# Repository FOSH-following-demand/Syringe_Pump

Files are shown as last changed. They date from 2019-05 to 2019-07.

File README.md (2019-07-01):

# Syringe Pump
<p align="center">
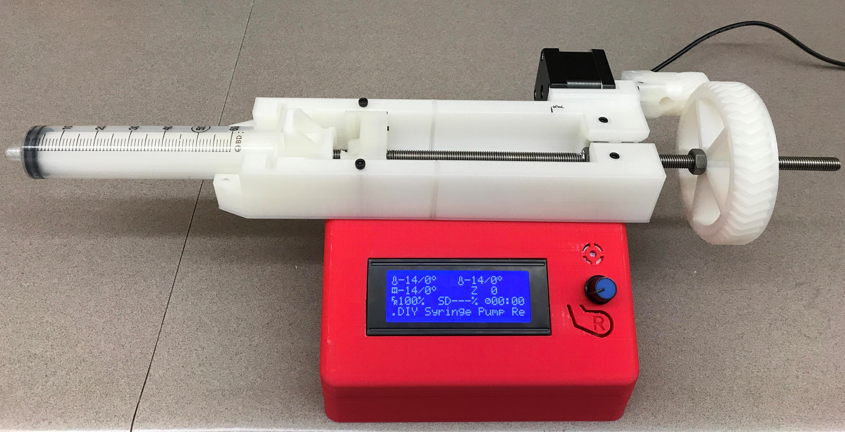
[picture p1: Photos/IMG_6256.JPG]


We are a team of 4 people from Utah, USA. We creating a open source DIY syringe pump from commonly available and 3D printed parts that allows for high accuracy and repeatability. We also want to make this project as simple as possible so that no specialized skills are required.

The syringe pump that will be built will then be able to be integrated with almost any commonly available desktop 3D printer to create a [bioprinter](https://github.com/FOSH-following-demand/Bioprinter).

We would like to give credit to Kira Puscha, Thomas J.Hinton, and Adam W.Feinberg at Carnegie for their work on the [Large volume syringe pump extruder for desktop 3D printers](https://www.sciencedirect.com/science/article/pii/S2468067217300822#!) that served for the basis and inspiration for this project

If you have any questions or get involved, get in contact with us via email at drewcliffporter@gmail.com

## Getting Started

Follow these links to learn about this project, and to get started building your own syringe pump!
- [Large Volume Syringe Pump Extruder](https://www.sciencedirect.com/science/article/pii/S2468067217300822#!)
- [Parts to purchase](Bill_of_Materials)
- [Parts to 3D print](3D_Printed_Parts.csv)
- [Assembly](Assembly_Instructions.md)
- [Troubleshooting](Troubleshooting.md)
- [Firmware](Firmware)
- [Calibration](Calibration.md)
- [Using your new pump](Getting_Started.md)
## Progress

Week 1:
- Identified parts to order
- Learned how to use Github (to an extent)
-

Week 2:
- Got parts in
- Started assembly of syringe pump
-

Week 3:
- Finished assembly of syringe pump
- Started Programing
- Began troubleshooting

Week 4:
- Continued programming
- began working on the bioprinter
- Printed Control Box

Week 5:
- Calibration
- Integration into the bioprinter
- Code Tweaks

Week 6:
- Started Bioprinting
- Failed at bioprinting
- Almost finished the GitHub repository

Week 7:
- Got some advice from Advanced BioMatrix
- Ordered a different gelatin
- Researched different "bioinks"
- Tried to print with different materials (agarose, calcium phosphate, frosting), but none worked

Week 8:
-
-
-

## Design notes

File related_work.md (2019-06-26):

# Related projects

Use this file to store updated information on projects similar to yours. You will start it on week 1 and probably keep updating it as you find more similar projects.

Make sure each reference meets the minimum requirements (url, active/non active, notes on how it's useful for you), and feel free to add other useful fields.

Look below for a template. For a markdown cheatsheet, check [this repo](https://github.com/adam-p/markdown-here/wiki/Markdown-Cheatsheet#tables).

| Project name  | URL           | Active/Not active | Notes - relevance |
| ------------- | ------------- | ----------------- | -------------- |
| Large volume syringe pump extruder for desktop 3D printers | https://www.sciencedirect.com/science/article/pii/S2468067217300822#! | Active | Favorite method so far, accurate dispensing of the liquid, requires less hardware to be purchased, only one size of syringe, retraction enabled, Doesn't work separate from a 3D printer |
| Open-Source Syringe Pump Library | https://www.academia.edu/8369549/Open-Source_Syringe_Pump_Library | Not Active | Can be used for any size syringe |
| Open-source syringe pump | https://www.appropedia.org/Open-source_syringe_pump | Active | Using similar method as we plan to use, however we believe ours will have a greater accuracy at small volumes, must have a computer to control, cannot be controlled with a Windows computer |

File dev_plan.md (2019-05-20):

# Development plan

Use this file to store your plan for the program. What are you going to do, in which order?

| Week        | Activities           | Who           |
| ----------- | -------------------- | ------------- |
| 1           | Create GitHub repo, familiarize with GitHub, first call with mentor, identify similar projects, identify parts to order  |Drew, All|
| 2           | Order parts, second call, more research into similar projects | Drew, All |
| 3           | Start Assembly, Start coding, Start designing/printing, third call | Drew, AJ, All |
| 4           | Finish assembly and code, start testing and calibration, fourth call | All |
| 5           | Finish testing and calibration, make any necessary changes, fifth call | All |
| 6           | Troubleshoot bioprints and create documentation for good bioprints, sixth call | Drew |
| 7           | Make sure the repository is accurate and informative, seventh call | All |
| 8           | Buffer week                     |               |

# Syringe Pump plan

We plan on using easy to use, off the shelf components, 3D printed parts, and easily accessible code to develop the pump. We want to create the pump in such a way that minimal skills will be required for the assembly and use. Therefore things such as soldering should be avoided. To avoid soldering we will be using an Arduino Mega board that has stepper motor drivers built in. We also want the unit to be self contained and not require the input from a computer to control the dispensing of the liquid.

 We also plan on using open sourced firmware that is originally for 3D printers for the syringe pump. That makes it so that we don't have to reinvent the wheel, and up to five syringe pumps can be controlled from a single control board. This also allows for upgrades to the pump if the user desires, such as endstops and thermal regulation. The use of 3D printer firmware allows for the user to create a program in the easy to learn language of G-Code that could complete a series of tasks, without the user having to interact with the pump controls.

 In harmony with the second part of our project, a 3D printed housing will be produced to house all of the electronics.

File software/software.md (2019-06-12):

The software for this pump is based on the open source firmware for 3D printers. The firmware we used is called Marlin, and can be found here http://marlinfw.org/. We used version 1.1 in this build, and made modifications to allow the firmware to best serve its purpose in this syringe pump.

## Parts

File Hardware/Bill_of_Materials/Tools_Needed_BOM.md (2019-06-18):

# Necessary

- M3 allen wrench
- M8 allen Wrench
- Drill
- 7/64th drill bit
- needle nose or slipjoint pliers

# Optional

- Tweezers

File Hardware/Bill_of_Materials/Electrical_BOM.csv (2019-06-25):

Item | Quantity | Cost | Source
MKS-Base v1.6 | 1 | 34.99 | https://www.amazon.com/BIQU-MKS-Base-Plate-Controller-Printer/dp/B076S2SDQ9
Smart Display | 1 | 10.99 | https://www.amazon.com/BIQU-Display-Controller-2004LCD-Adapter/dp/B01FLU9X5Q
NEMA 17 Stepper Motor | 1 | 9.99 | https://www.amazon.com/UsongShine-Nema17-Stepper-17HS4401S-Printer/dp/B0787BQ4WH?s=gateway
Power Supply 12V 5A | 1 | 7.95 | https://www.ebay.com/itm/AC100-240V-To-DC-12V-1-2-3-5-6-8A-US-Power-Supply-Adapter-Transformer-LED-Strip/202127822979
TOTAL |  | 63.92
Note: A smaller Arduino such as the Arduino Uno could be used instead of the MKS-Base.
But if this approach is used separate stepper motor drivers must be purchased
and the code provided here might not work. The price ends up being comparable
in the end for both methods.

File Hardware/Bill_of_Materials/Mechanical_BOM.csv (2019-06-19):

Item | Quantity | Cost | Source
Double Shielded Ball Bearings | 2 | 5.98 | https://www.amazon.com/Onwon-Pieces-Skateboard-Bearings-Miniature/dp/B07LCJ9VM6?s=gateway
M8 2.4 mm Steel Hex Nuts | 4 | 4.84 | https://www.mcmaster.com/90592a022
M8 Brass Hex Nuts | 2 | 0.55 | https://www.fastenal.com/products/details/MN2580000BR0000
M8 1.25 by 300mm Threaded Rod Stainless Steel | 1 | 7.78 | https://www.mcmaster.com/90024a229
M3 10 mm Socket Head Screws (Hex Bolts) | 10 | 7.36 | https://www.mcmaster.com/91290a115
M3 16 mm Socket Head Screws (i.e. Hex Bolts) | 4 | 8.87 | https://www.mcmaster.com/91290a120
M3 8 mm Socket Head Screws (i.e. Hex Bolts) | 6 | 7.12 | https://www.mcmaster.com/91290a113
M3 45 mm Partially-Threaded Socket Head Screws (i.e. Hex Bolts) | 4 | 3.65 | https://www.mcmaster.com/91290a079
M3 Hex Nuts | 16 | 0.88 | https://www.mcmaster.com/90592a085
M3 x 8mm OD washers | 4 | 0.98 | https://www.mcmaster.com/93849a101
60 mL Luer-Lock BD Syringe | 1 | 33.31 | https://www.amazon.com/BD-60ml-CC-SYRINGE-ONLY/dp/B01EGL2WNG?s=industrial
PLA 1.75mm | 1 | 15-30
TOTAL |  | ~100
NOTE: |  |  | All the prices are for the minimum order requirement. Therefore the overall cost for one syringe pump is less than reported here. The parts also do not have to be bought from the sources listed here and could be found from a cheaper source.

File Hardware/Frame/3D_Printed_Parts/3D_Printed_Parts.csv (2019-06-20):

Name | Notes | Source
MKS Base 1.5 based desktop controller cabinet | Print with more than 3 walls and top/bottom layers. Supports are needed for the top | https://www.thingiverse.com/thing:3156697
Large Volume Syringe Pump Extruder (LVE) | Follow directions found here https://www.sciencedirect.com/science/article/pii/S2468067217300822#! | https://3dprint.nih.gov/discover/3DPX-008366

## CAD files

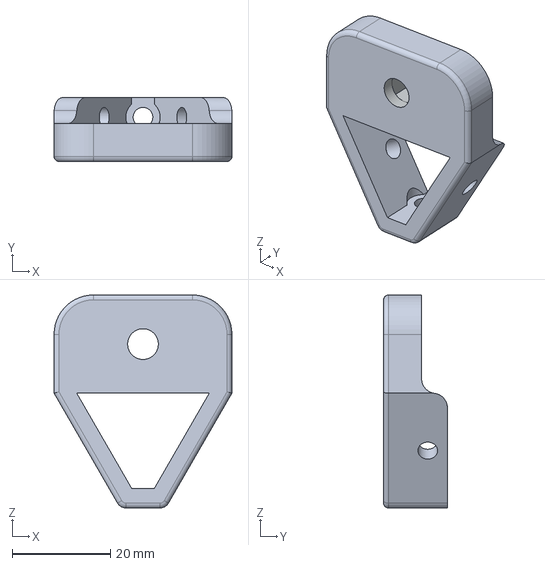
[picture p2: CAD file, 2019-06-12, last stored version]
Hardware/Frame/3D_Printed_Parts/Needle Carriage Mount.stp
36.2 x 13.0 x 43.4 mm

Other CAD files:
Hardware/Frame/3D_Printed_Parts/Needle Carriage Mount.stl
Hardware/Frame/Needle Carriage Mount.stl

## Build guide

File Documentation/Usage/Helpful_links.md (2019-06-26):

Syringe pump body assembly
https://www.youtube.com/watch?v=Zy11gkKKrqw

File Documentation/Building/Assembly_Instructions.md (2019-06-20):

# Steps

1. Purchase all of the parts from the [Electrical bill of materials](https://github.com/FOSH-following-demand/Syringe_Pump/blob/master/Hardware/Bill_of_Materials/Electrical_BOM.csv) and the [Mechanical bill of materials](https://github.com/FOSH-following-demand/Syringe_Pump/blob/master/Hardware/Bill_of_Materials/Mechanical_BOM.csv)
1. 3D print all the necessary [parts](https://github.com/FOSH-following-demand/Syringe_Pump/blob/master/Hardware/Frame/3D_Printed_Parts/3D_Printed_Parts.csv)
1. Assemble the syringe pump body by following the directions found [here](https://www.sciencedirect.com/science/article/pii/S2468067217300822#!). Please refer to [troubleshooting](Troubleshooting.md) for any problems that you encounter as we discovered a few quirks with the assembly described in the link.
1. Remove the control knob from the Smart Display

<p align="center">
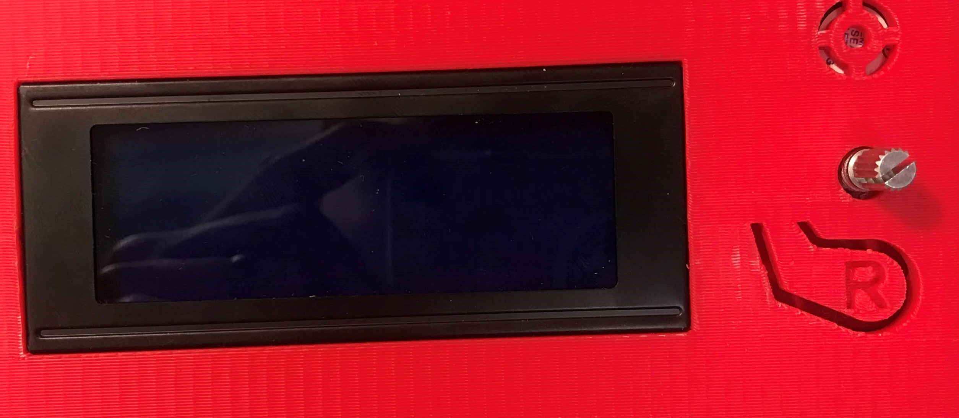
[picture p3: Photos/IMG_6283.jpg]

<h6 align="center">Removed control knob</h6>

1. Attach the MKS-Base v1.6 and the Smart Display to the controller cabinet using M3 X 8 screws
  -Note: Depending on the tolerances and nuances of every 3D printer, and different part manufacturers, the fit of the MKS-Base and Smart Display might be a little off. Only two screws are necessary to hold the parts in place, and some of the screen hole may need to be shaved down with a razor blade for the screen to fit.
1. Replace the control knob

<p align="center">
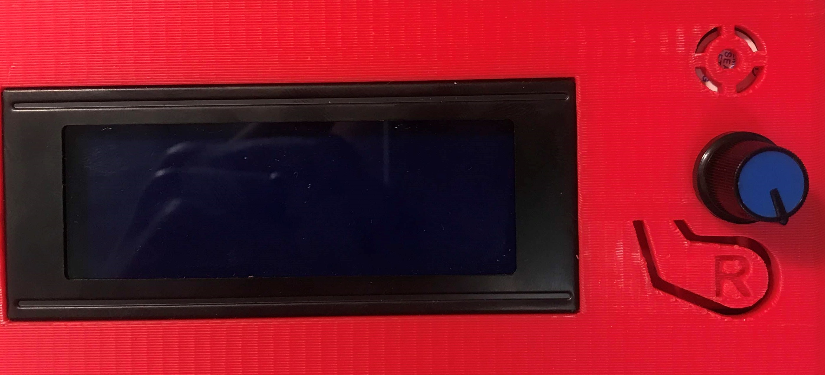
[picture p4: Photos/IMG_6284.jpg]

<h6 align="center">Replaced control knob</h6>

1. If the power supply has an extendable plug, attach it to the board and feed the wires through the power port, otherwise cut off the end of the power supply, strip the wires, and attach the exposed leads to the board

  <p align="center">
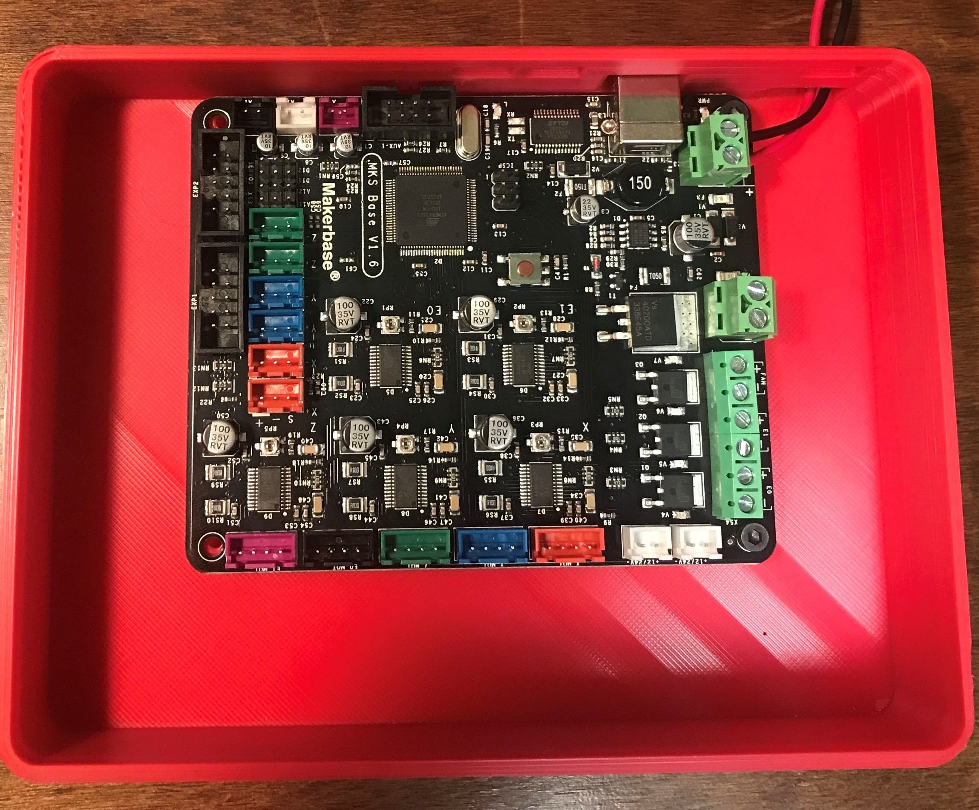
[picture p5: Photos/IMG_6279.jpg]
  
  <h6 align="center">MKS-Base in the case with power supply attached</h6>
  <p align="center">
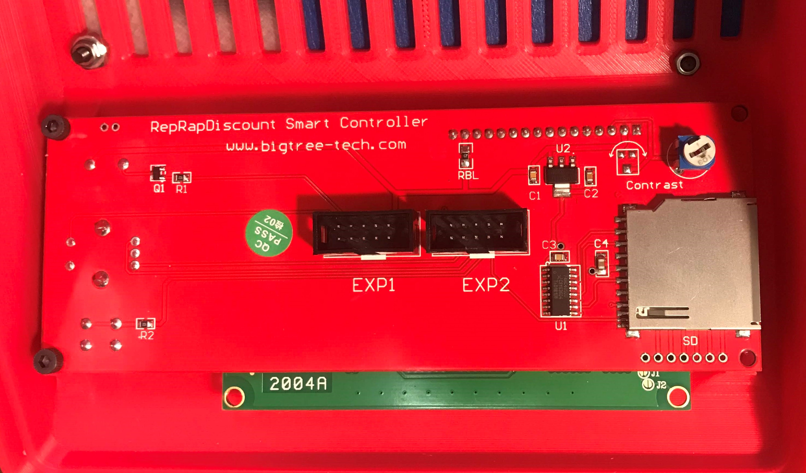
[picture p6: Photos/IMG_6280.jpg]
  
  <h6 align="center">Fasten the screen to the case</h6>

1. Place syringe pump body on the top of the case. Put two M3 X 45 screws through the two holes by the bearing and feed them through the last slot on the case. Attach with washers and M3 nuts. Note: I did not have any M3 nuts on hand, so I improvised with some larger nuts to hold mine in place.
1. Drill two holes with the 7/64th drill bit towards the front of the pump body, and drill through the pump and the case. Push two M3 X 45 screws in and fasten with M3 nuts and washers. Note: If you drill too close to the edge of the case, you will be unable to put a nut and washer on that screw.

<p align="center">
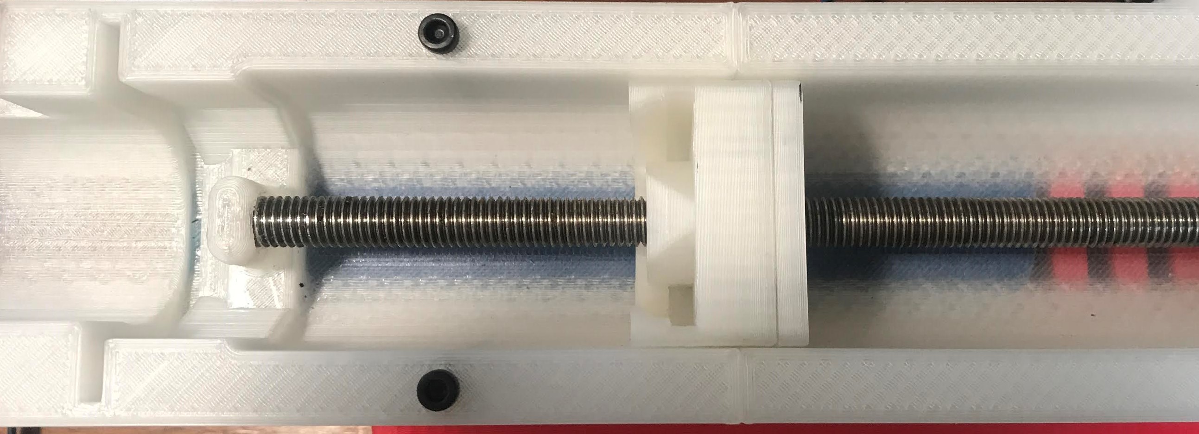
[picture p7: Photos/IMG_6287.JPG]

<h6 align="center">Screws drilled and attached through the pump body</h6>
<p align="center">
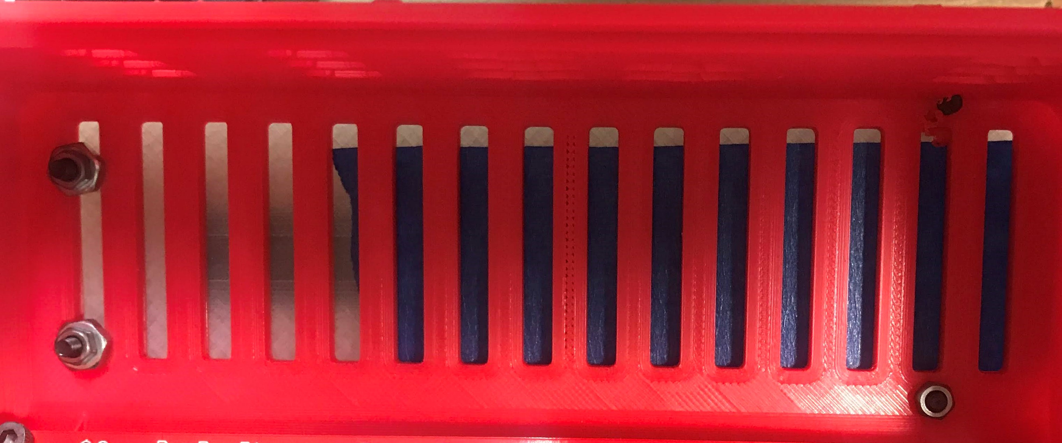
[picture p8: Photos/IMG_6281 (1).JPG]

<h6 align="center">Inside of case, where the body is attached to the electronics case</h6>

1. Plug the screen cables in and plug the stepper motor cable in to the E0 port as show in the picture

<p align="center">
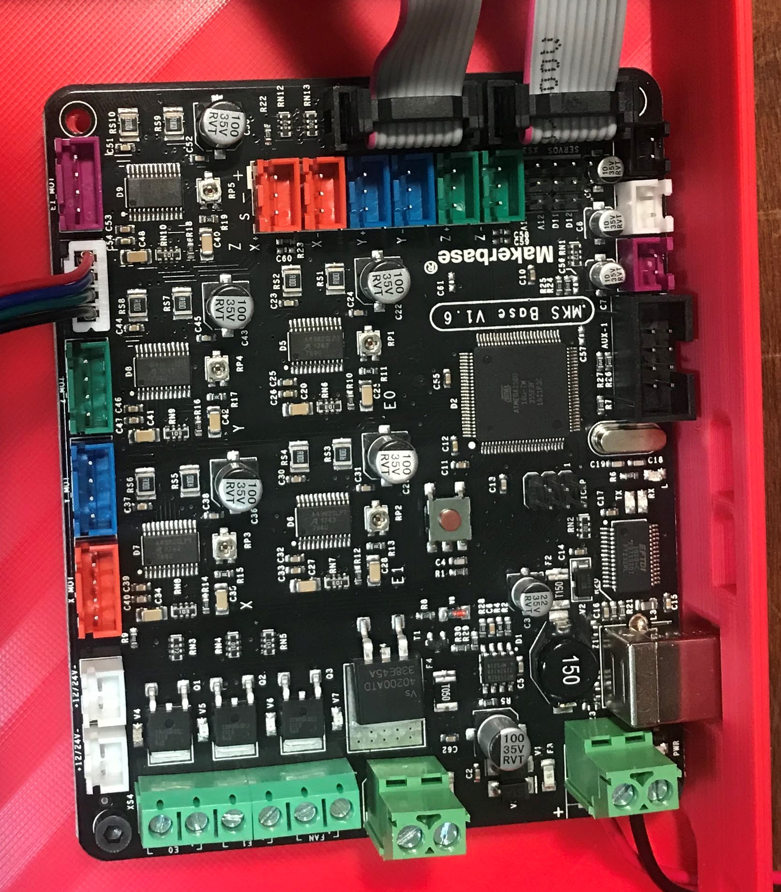
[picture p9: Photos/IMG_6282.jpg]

<h6 align="center">Cables plugged into the MKS-Base</h6>

1. Plug the other end of the screen cable into the Smart Display. Ensure that the EXP1 and EXP2 ports on the display are connected to the same ports on the board

<p align="center">
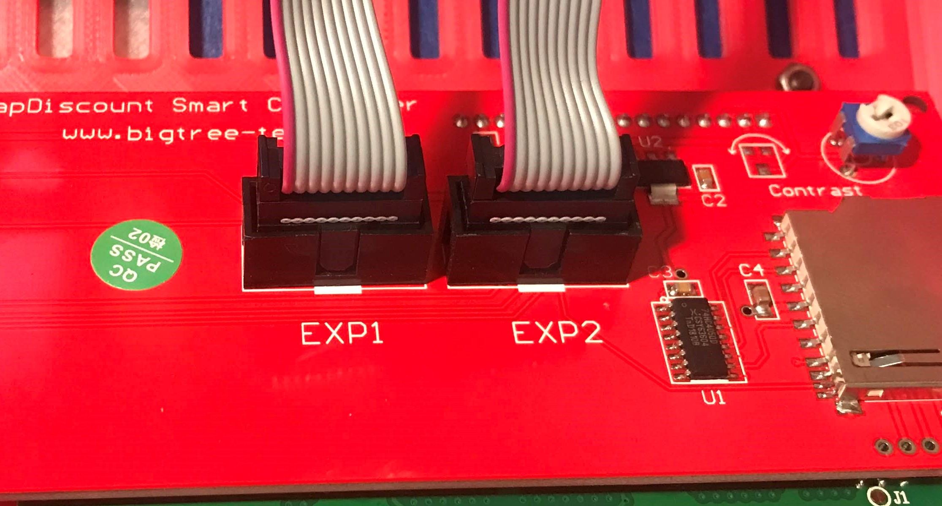
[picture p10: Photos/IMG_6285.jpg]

<h6 align="center">Cables plugged into the Smart Display</h6>

1. Feed the stepper motor cable through one of the slots in the back of the case, and connect it to the stepper motor on the pump body

<p align="center">
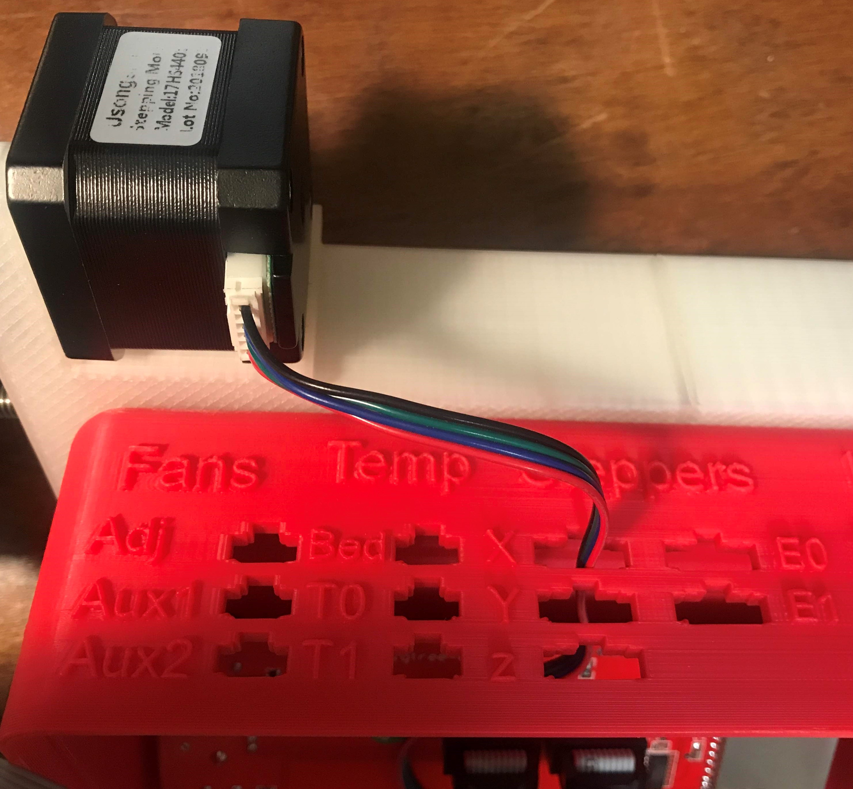
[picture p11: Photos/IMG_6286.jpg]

<h6 align="center">Stepper motor cable connected</h6>

1. Plug the power supply in and ensure that everything turns on and that the stepper motor rotates
1. Close the case
1. Connect the computer cable to the port on the back of the case, and connect the USB to your computer.
1. Using the [Arduino IDE](https://www.arduino.cc/en/Main/Software) upload the [firmware](https://github.com/FOSH-following-demand/Syringe_Pump/tree/master/software/MCU/Firmware/Syringe_Pump) by following these [instructions](https://www.arduino.cc/en/Guide/ArduinoMega2560#toc2)
1. Follow the [instructions](https://github.com/FOSH-following-demand/Syringe_Pump/blob/master/Documentation/Usage/Getting%20Started) to start using your syringe pump
1. [Calibrate](Calibration.md) your syringe pump
1. Do awesome science!!!

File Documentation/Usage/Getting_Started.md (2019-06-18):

# Getting Started

### Initialize EEPROM
After you have uploaded the firmware you must initialize EEPROM for the changes to take effect. Do this after any firmware is uploaded from the computer to the pump
1. Plug in your syringe pump
2. Press the control knob to access the menu
3. Go to Control > Initialize EEPROM > Initialize EEPROM. You should hear a beep

### Using the pump

Using the pump is very simple. The pump can push out volumes in three different step sizes: 5mL, 1mL or 0.5mL at a time.
1. Press the control knob to access the menu
2. Go to Prepare > Pump > Pump E0
 -All of the other options under pump are for the other ports on the board. These can be used to control multiple syringe pumps from one control unit. The name of the option corresponds with the name of the port that subsequent pumps would be connected to
3. Select the volume size you would like to pump
4. Turn the knob clockwise to pump out liquid and turn it counterclockwise to suck in liquid.

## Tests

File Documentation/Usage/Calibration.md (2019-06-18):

# Calibration

While general values for the number of steps per millimeter will give you decent accuracy, it is necessary to calibrate and change the steps per millimeter for the best accuracy. There are many online guides for calibrating the steps/mm for 3D printers, such as this one found here at All3DP (https://all3dp.com/2/extruder-calibration-6-easy-steps-2/). However, we will have to change a few things to calibrate the syringe pump, since it is a little different from a 3D printer.

# Supplies Needed

- Scale
- Water Container
- Distilled Water
- Needle or Pipette Tip
- Tubing

# Steps

1. Plug in syringe pump
2. Fill syringe with distilled water
3. Attach tubing to the pump with a needle/pipette tip on the other end of the tubing
<p align="left">
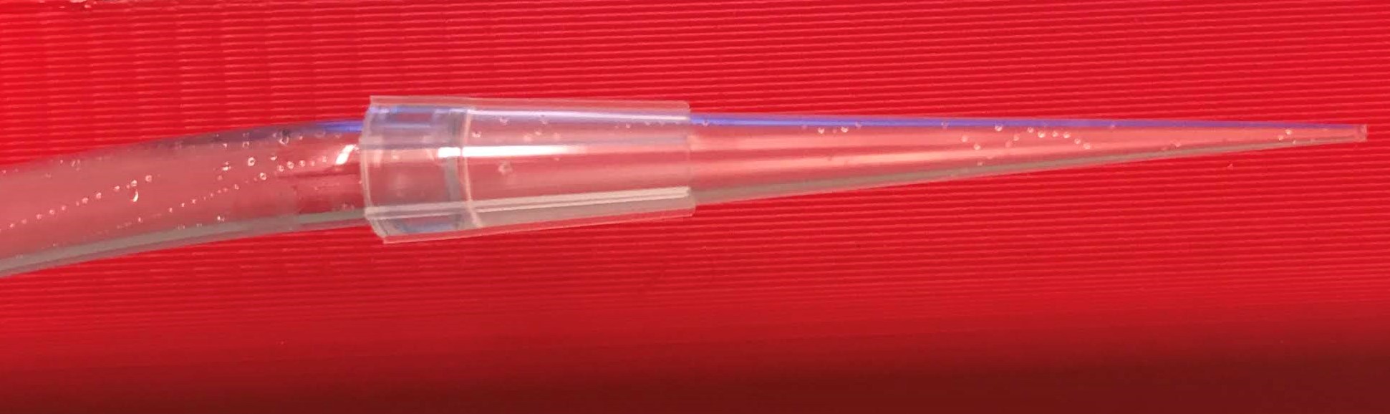
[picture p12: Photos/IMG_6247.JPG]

<h6 align="left">Attached a pipette tip for calibration</h6>

4. Prime the pump by pumping water till it starts to drip out of the needle
5. Place water container on the scale and tare the scale
6. Pump out 5 mL of water into the container and record the weight
7. Tare the scale again and repeat step 6 five more times
8. Take an average of all six measurements

The density of pure water is 1 gram per cubic centimeter (g/cm^3). Since 1 mL is one cubic centimeter, we can calculate exactly how much water was pumped out each time and adjust accordingly.

For example we will use 4.8 grams as our average.

Determine how many steps per millimeter the motor took to pump out 4.8 g of water. Multiply the number of steps (This can be found under Control > Motion > Steps/mm) by the number of milliliters that were supposed to be extruded.

  [Steps/mm] x 5 mL = Steps taken

Then we will use the number of steps taken to determine the new number of steps needed.

  [Steps taken] / [Average weight in grams] = [New steps per millimeter value]

The combined equation is:

  [Original Steps/mm] x [Volume supposed to be pumped] / [Averaged weight in grams] = [New steps/mm value]

The new steps/mm value can then be changed by following the same path, and then twisting the control knob until the desired value is set. It can also be changed by changing the appropriate value in the firmware.  

NOTE: If the new steps/mm value is not saved by going Control > Store Settings the new steps/mm value will have to be entered every time that the pump is turned on.

It may be necessary to perform this calibration multiple times to ensure that the calibration is correct. It is also advisable to perform the calibration for all three main volumes (5, 1, 0.5 mL) and then averaging the steps/mm value calculated for each volume. This is because the steps/mm required often increase as smaller volumes are extruded.

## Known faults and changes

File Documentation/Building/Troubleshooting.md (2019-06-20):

# Possible problems.

1. Screen not turning on:
Some users of the MKS Base V1.6 have reported that the screen will not turn on. This happened for us as well. We Solved the problem by cutting off the plastic key on one end of each of the screen cables, and rotating the connector in the socket. This solved the problem.

1. Some of the parts from the LVE were not necessary to print. Please evaluate each part and decide if it is necessary for your individual setup. We found that the Syringe guide and syringe collar did not adequately secure the syringe, and therefore were not necessary. Also the Needle adapter, needle collar, 250 um Needle jig, 18-guage needle jig short, and 18-guage needle jig extended should only be evaluated for printing if you plan on also using the syringe pump in a bioprinter.

1. The 16mm screws were too long for our stepper motor. We assumed that the manufacturers have different hole depths. So we solved the problem by putting two nuts on the screws before screwing them into the motors.

1. The 17-guage needle did not fit as snugly as we would have liked, and so we used a small dab of super glue to seal the needle to the tube. Just make sure not to seal the needle.

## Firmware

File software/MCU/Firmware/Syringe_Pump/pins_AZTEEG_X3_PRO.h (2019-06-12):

/**
 * Marlin 3D Printer Firmware
 * Copyright (C) 2016 MarlinFirmware [https://github.com/MarlinFirmware/Marlin]
 *
 * Based on Sprinter and grbl.
 * Copyright (C) 2011 Camiel Gubbels / Erik van der Zalm
 *
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
 */

/**
 * AZTEEG_X3_PRO (Arduino Mega) pin assignments
 */

#if HOTENDS > 5 || E_STEPPERS > 5
  #error "Azteeg X3 Pro supports up to 5 hotends / E-steppers. Comment out this line to continue."
#endif

#if ENABLED(CASE_LIGHT_ENABLE) && !PIN_EXISTS(CASE_LIGHT)
  #define CASE_LIGHT_PIN 44     // Define before RAMPS pins include
#endif

#define BOARD_NAME "Azteeg X3 Pro"

#include "pins_RAMPS.h"

#ifndef __AVR_ATmega2560__
  #error "Oops! Make sure you have 'Arduino Mega 2560' selected from the 'Tools -> Boards' menu."
#endif

// DIGIPOT slave addresses
#define DIGIPOT_I2C_ADDRESS_A 0x2C   // unshifted slave address for first DIGIPOT 0x2C (0x58 <- 0x2C << 1)
#define DIGIPOT_I2C_ADDRESS_B 0x2E   // unshifted slave address for second DIGIPOT 0x2E (0x5C <- 0x2E << 1)

//
// Servos
//
// Tested this pin with bed leveling on a Delta with 1 servo.
// Physical wire attachment on EXT1: GND, 5V, D47.
//
#undef SERVO0_PIN
#define SERVO0_PIN         47

//
// Limit Switches
//
// Swap the MIN and MAX endstop pins because the X3 Pro comes with only
// MIN endstop pin headers soldered onto the board.
//
#if ENABLED(DELTA)
  #undef X_MIN_PIN
  #undef X_MAX_PIN
  #undef Y_MIN_PIN
  #undef Y_MAX_PIN
  #undef Z_MIN_PIN
  #undef Z_MAX_PIN

  #define X_MIN_PIN         2
  #define X_MAX_PIN         3
  #define Y_MIN_PIN        15
  #define Y_MAX_PIN        14
  #define Z_MIN_PIN        19
  #define Z_MAX_PIN        18
#endif

//
// Z Probe (when not Z_MIN_PIN)
//
#ifndef Z_MIN_PROBE_PIN
  #define Z_MIN_PROBE_PIN  18
#endif

//
// Steppers
//
#define E2_STEP_PIN        23
#define E2_DIR_PIN         25
#define E2_ENABLE_PIN      40

#define E3_STEP_PIN        27
#define E3_DIR_PIN         29
#define E3_ENABLE_PIN      41

#define E4_STEP_PIN        43
#define E4_DIR_PIN         37
#define E4_ENABLE_PIN      42

//
// Temperature Sensors
//
#define TEMP_2_PIN         12   // Analog Input
#define TEMP_3_PIN         11   // Analog Input
#define TEMP_4_PIN         10   // Analog Input
#define TC1                 4   // Analog Input (Thermo couple on Azteeg X3Pro)
#define TC2                 5   // Analog Input (Thermo couple on Azteeg X3Pro)

//
// Heaters / Fans
//
#define HEATER_2_PIN       16
#define HEATER_3_PIN       17
#define HEATER_4_PIN        4
#define HEATER_5_PIN        5
#define HEATER_6_PIN        6
#define HEATER_7_PIN       11

#undef FAN_PIN
#define FAN_PIN             6   // Part Cooling System

#ifndef CONTROLLER_FAN_PIN
  #define CONTROLLER_FAN_PIN 4   // Pin used for the fan to cool motherboard (-1 to disable)
#endif

// Fans/Water Pump to cool the hotend cool side.
#define ORIG_E0_AUTO_FAN_PIN 5
#define ORIG_E1_AUTO_FAN_PIN 5
#define ORIG_E2_AUTO_FAN_PIN 5
#define ORIG_E3_AUTO_FAN_PIN 5

//
// LCD / Controller
//
#undef BEEPER_PIN
#define BEEPER_PIN         33

#if ENABLED(VIKI2) || ENABLED(miniVIKI)
  #undef SD_DETECT_PIN
  #define SD_DETECT_PIN    49   // For easy adapter board
  #undef BEEPER_PIN
  #define  BEEPER_PIN      12   // 33 isn't physically available to the LCD display
#else
  #define STAT_LED_RED_PIN  32
  #define STAT_LED_BLUE_PIN 35
#endif

//
// Misc. Functions
//
#if ENABLED(CASE_LIGHT_ENABLE)  && PIN_EXISTS(CASE_LIGHT) && defined(DOGLCD_A0) && DOGLCD_A0 == CASE_LIGHT_PIN
  #undef DOGLCD_A0              // Steal pin 44 for the case light; if you have a Viki2 and have connected it
  #define DOGLCD_A0        57   // following the Panucatt wiring diagram, you may need to tweak these pin assignments
                                // as the wiring diagram uses pin 44 for DOGLCD_A0
#endif

//
// M3/M4/M5 - Spindle/Laser Control
//
#undef SPINDLE_LASER_PWM_PIN    // Definitions in pins_RAMPS.h are no good with the AzteegX3pro board
#undef SPINDLE_LASER_ENABLE_PIN
#undef SPINDLE_DIR_PIN

#if ENABLED(SPINDLE_LASER_ENABLE)   // EXP2 header
  #if ENABLED(VIKI2) || ENABLED(miniVIKI)
    #undef BTN_EN2
    #define BTN_EN2             31   // need 7 for the spindle speed PWM
  #endif
  #define SPINDLE_LASER_PWM_PIN     7   // must have a hardware PWM
  #define SPINDLE_LASER_ENABLE_PIN 20   // Pin should have a pullup!
  #define SPINDLE_DIR_PIN          21
#endif

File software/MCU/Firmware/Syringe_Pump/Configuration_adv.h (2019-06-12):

/**
 * Marlin 3D Printer Firmware
 * Copyright (C) 2016 MarlinFirmware [https://github.com/MarlinFirmware/Marlin]
 *
 * Based on Sprinter and grbl.
 * Copyright (C) 2011 Camiel Gubbels / Erik van der Zalm
 *
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
 */

/**
 * Configuration_adv.h
 *
 * Advanced settings.
 * Only change these if you know exactly what you're doing.
 * Some of these settings can damage your printer if improperly set!
 *
 * Basic settings can be found in Configuration.h
 *
 */
#ifndef CONFIGURATION_ADV_H
#define CONFIGURATION_ADV_H
#define CONFIGURATION_ADV_H_VERSION 010107

// @section temperature

//===========================================================================
//=============================Thermal Settings  ============================
//===========================================================================

//
// Hephestos 2 24V heated bed upgrade kit.
// https://store.bq.com/en/heated-bed-kit-hephestos2
//
//#define HEPHESTOS2_HEATED_BED_KIT
#if ENABLED(HEPHESTOS2_HEATED_BED_KIT)
  #undef TEMP_SENSOR_BED
  #define TEMP_SENSOR_BED 70
  #define HEATER_BED_INVERTING true
#endif

#if DISABLED(PIDTEMPBED)
  #define BED_CHECK_INTERVAL 5000 // ms between checks in bang-bang control
  #if ENABLED(BED_LIMIT_SWITCHING)
    #define BED_HYSTERESIS 2 // Only disable heating if T>target+BED_HYSTERESIS and enable heating if T>target-BED_HYSTERESIS
  #endif
#endif

/**
 * Thermal Protection provides additional protection to your printer from damage
 * and fire. Marlin always includes safe min and max temperature ranges which
 * protect against a broken or disconnected thermistor wire.
 *
 * The issue: If a thermistor falls out, it will report the much lower
 * temperature of the air in the room, and the the firmware will keep
 * the heater on.
 *
 * The solution: Once the temperature reaches the target, start observing.
 * If the temperature stays too far below the target (hysteresis) for too
 * long (period), the firmware will halt the machine as a safety precaution.
 *
 * If you get false positives for "Thermal Runaway", increase
 * THERMAL_PROTECTION_HYSTERESIS and/or THERMAL_PROTECTION_PERIOD
 */
#if ENABLED(THERMAL_PROTECTION_HOTENDS)
  #define THERMAL_PROTECTION_PERIOD 60        // Seconds
  #define THERMAL_PROTECTION_HYSTERESIS 10    // Degrees Celsius

  /**
   * Whenever an M104, M109, or M303 increases the target temperature, the
   * firmware will wait for the WATCH_TEMP_PERIOD to expire. If the temperature
   * hasn't increased by WATCH_TEMP_INCREASE degrees, the machine is halted and
   * requires a hard reset. This test restarts with any M104/M109/M303, but only
   * if the current temperature is far enough below the target for a reliable
   * test.
   *
   * If you get false positives for "Heating failed", increase WATCH_TEMP_PERIOD
   * and/or decrease WATCH_TEMP_INCREASE. WATCH_TEMP_INCREASE should not be set
   * below 2.
   */
  #define WATCH_TEMP_PERIOD 30                // Seconds
  #define WATCH_TEMP_INCREASE 2               // Degrees Celsius
#endif

/**
 * Thermal Protection parameters for the bed are just as above for hotends.
 */
#if ENABLED(THERMAL_PROTECTION_BED)
  #define THERMAL_PROTECTION_BED_PERIOD 60    // Seconds
  #define THERMAL_PROTECTION_BED_HYSTERESIS 4 // Degrees Celsius

  /**
   * As described above, except for the bed (M140/M190/M303).
   */
  #define WATCH_BED_TEMP_PERIOD 120                // Seconds
  #define WATCH_BED_TEMP_INCREASE 2               // Degrees Celsius
#endif

#if ENABLED(PIDTEMP)
  // this adds an experimental additional term to the heating power, proportional to the extrusion speed.
  // if Kc is chosen well, the additional required power due to increased melting should be compensated.
  //#define PID_EXTRUSION_SCALING
  #if ENABLED(PID_EXTRUSION_SCALING)
    #define DEFAULT_Kc (100) //heating power=Kc*(e_speed)
    #define LPQ_MAX_LEN 50
  #endif
#endif

/**
 * Automatic Temperature:
 * The hotend target temperature is calculated by all the buffered lines of gcode.
 * The maximum buffered steps/sec of the extruder motor is called "se".
 * Start autotemp mode with M109 S<mintemp> B<maxtemp> F<factor>
 * The target temperature is set to mintemp+factor*se[steps/sec] and is limited by
 * mintemp and maxtemp. Turn this off by executing M109 without F*
 * Also, if the temperature is set to a value below mintemp, it will not be changed by autotemp.
 * On an Ultimaker, some initial testing worked with M109 S215 B260 F1 in the start.gcode
 */
#define AUTOTEMP
#if ENABLED(AUTOTEMP)
  #define AUTOTEMP_OLDWEIGHT 0.98
#endif

// Show extra position information in M114
//#define M114_DETAIL

// Show Temperature ADC value
// Enable for M105 to include ADC values read from temperature sensors.
//#define SHOW_TEMP_ADC_VALUES

/**
 * High Temperature Thermistor Support
 *
 * Thermistors able to support high temperature tend to have a hard time getting
 * good readings at room and lower temperatures. This means HEATER_X_RAW_LO_TEMP
 * will probably be caught when the heating element first turns on during the
 * preheating process, which will trigger a min_temp_error as a safety measure
 * and force stop everything.
 * To circumvent this limitation, we allow for a preheat time (during which,
 * min_temp_error won't be triggered) and add a min_temp buffer to handle
 * aberrant readings.
 *
 * If you want to enable this feature for your hotend thermistor(s)
 * uncomment and set values > 0 in the constants below
 */

// The number of consecutive low temperature errors that can occur
// before a min_temp_error is triggered. (Shouldn't be more than 10.)
//#define MAX_CONSECUTIVE_LOW_TEMPERATURE_ERROR_ALLOWED 0

// The number of milliseconds a hotend will preheat before starting to check
// the temperature. This value should NOT be set to the time it takes the
// hot end to reach the target temperature, but the time it takes to reach
// the minimum temperature your thermistor can read. The lower the better/safer.
// This shouldn't need to be more than 30 seconds (30000)
//#define MILLISECONDS_PREHEAT_TIME 0

// @section extruder

// Extruder runout prevention.
// If the machine is idle and the temperature over MINTEMP
// then extrude some filament every couple of SECONDS.
//#define EXTRUDER_RUNOUT_PREVENT
#if ENABLED(EXTRUDER_RUNOUT_PREVENT)
  #define EXTRUDER_RUNOUT_MINTEMP 190
  #define EXTRUDER_RUNOUT_SECONDS 30
  #define EXTRUDER_RUNOUT_SPEED 1500  // mm/m
  #define EXTRUDER_RUNOUT_EXTRUDE 5   // mm
#endif

// @section temperature

// Calibration for AD595 / AD8495 sensor to adjust temperature measurements.
// The final temperature is calculated as (measuredTemp * GAIN) + OFFSET.
#define TEMP_SENSOR_AD595_OFFSET  0.0
#define TEMP_SENSOR_AD595_GAIN    1.0
#define TEMP_SENSOR_AD8495_OFFSET 0.0
#define TEMP_SENSOR_AD8495_GAIN   1.0

/**
 * Controller Fan
 * To cool down the stepper drivers and MOSFETs.
 *
 * The fan will turn on automatically whenever any stepper is enabled
 * and turn off after a set period after all steppers are turned off.
 */
//#define USE_CONTROLLER_FAN
#if ENABLED(USE_CONTROLLER_FAN)
  //#define CONTROLLER_FAN_PIN -1        // Set a custom pin for the controller fan
  #define CONTROLLERFAN_SECS 60          // Duration in seconds for the fan to run after all motors are disabled
  #define CONTROLLERFAN_SPEED 255        // 255 == full speed
#endif

// When first starting the main fan, run it at full speed for the
// given number of milliseconds.  This gets the fan spinning reliably
// before setting a PWM value. (Does not work with software PWM for fan on Sanguinololu)
//#define FAN_KICKSTART_TIME 100

// This defines the minimal speed for the main fan, run in PWM mode
// to enable uncomment and set minimal PWM speed for reliable running (1-255)
// if fan speed is [1 - (FAN_MIN_PWM-1)] it is set to FAN_MIN_PWM
//#define FAN_MIN_PWM 50

// @section extruder

/**
 * Extruder cooling fans
 *
 * Extruder auto fans automatically turn on when their extruders'
 * temperatures go above EXTRUDER_AUTO_FAN_TEMPERATURE.
 *
 * Your board's pins file specifies the recommended pins. Override those here
 * or set to -1 to disable completely.
 *
 * Multiple extruders can be assigned to the same pin in which case
 * the fan will turn on when any selected extruder is above the threshold.
 */
#define E0_AUTO_FAN_PIN -1
#define E1_AUTO_FAN_PIN -1
#define E2_AUTO_FAN_PIN -1
#define E3_AUTO_FAN_PIN -1
#define E4_AUTO_FAN_PIN -1
#define CHAMBER_AUTO_FAN_PIN -1
#define EXTRUDER_AUTO_FAN_TEMPERATURE 50
#define EXTRUDER_AUTO_FAN_SPEED   255  // == full speed

/**
 * Part-Cooling Fan Multiplexer
 *
 * This feature allows you to digitally multiplex the fan output.
 * The multiplexer is automatically switched at tool-change.
 * Set FANMUX[012]_PINs below for up to 2, 4, or 8 multiplexed fans.
 */
#define FANMUX0_PIN -1
#define FANMUX1_PIN -1
#define FANMUX2_PIN -1

/**
 * M355 Case Light on-off / brightness
 */
//#define CASE_LIGHT_ENABLE
#if ENABLED(CASE_LIGHT_ENABLE)
  //#define CASE_LIGHT_PIN 4                  // Override the default pin if needed
  #define INVERT_CASE_LIGHT false             // Set true if Case Light is ON when pin is LOW
  #define CASE_LIGHT_DEFAULT_ON true          // Set default power-up state on
  #define CASE_LIGHT_DEFAULT_BRIGHTNESS 105   // Set default power-up brightness (0-255, requires PWM pin)
  //#define MENU_ITEM_CASE_LIGHT              // Add a Case Light option to the LCD main menu
  //#define CASE_LIGHT_USE_NEOPIXEL           // Use Neopixel LED as case light, requires NEOPIXEL_LED.
  #if ENABLED(CASE_LIGHT_USE_NEOPIXEL)
    #define CASE_LIGHT_NEOPIXEL_COLOR { 255, 255, 255, 255 } // { Red, Green, Blue, White }
  #endif
#endif

//===========================================================================
//============================ Mechanical Settings ==========================
//===========================================================================

// @section homing

// If you want endstops to stay on (by default) even when not homing
// enable this option. Override at any time with M120, M121.
//#define ENDSTOPS_ALWAYS_ON_DEFAULT

// @section extras

//#define Z_LATE_ENABLE // Enable Z the last moment. Needed if your Z driver overheats.
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

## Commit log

2019-05-15 Create Assembly Instructions
2019-05-15 Create Bill of Materials
2019-05-15 added folders and files
    [Electrical_BOM.csv, Mechanical_BOM.csv, Tools_Needed_BOM.csv]
2019-05-20 updated bill of materials
    [Electrical_BOM.csv, Mechanical_BOM.csv]
2019-06-10 Updated progress and made calibration documentation
2019-06-12 added firmware and updated bom
    [Mechanical_BOM.csv, Tools_Needed_BOM.csv]
2019-06-12 lots of updates
    [Mechanical_BOM.csv, Needle Carriage Mount.stl, Needle Carriage Mount.stp, Tools_Needed_BOM.csv]
2019-06-18 general updates
    [Mechanical_BOM.csv]
2019-06-18 tools needed
    [Tools_Needed_BOM.csv]
2019-06-18 3D printed parts
    [3D_Printed_Parts.csv]
2019-06-18 new folder
    [3D_Printed_Parts.csv, Needle Carriage Mount.stl, Needle Carriage Mount.stp]
2019-06-18 pictures and assembly
    [Needle Carriage Mount.stl, Needle Carriage Mount.stp]
2019-06-18 assembly instructions
2019-06-18 Update Assembly Instructions.md
2019-06-18 updated calibration and assembly
2019-11-16 Create open knowledge manifest for syringe pump
    I'm working with a group of people to make hardware easy to discover.
    Named [Open Know How](https://openknowhow.org/) we've come up with a system where a simple file with metadata about a certain project would live in the project documentation page.
    From there we are working to create a web-crawler that is going to find these files and index them (the ultimate goal would be to have something like a "hardware" tab on google search (as other searc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
    I took the liberty of creating one of these files for your project, with the bare minimum for it to be indexed in the future! I hope you don't mind! (it is just this .yml file that s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

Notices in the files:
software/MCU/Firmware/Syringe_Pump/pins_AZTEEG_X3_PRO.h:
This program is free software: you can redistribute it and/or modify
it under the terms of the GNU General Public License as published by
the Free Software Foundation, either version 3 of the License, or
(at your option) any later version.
